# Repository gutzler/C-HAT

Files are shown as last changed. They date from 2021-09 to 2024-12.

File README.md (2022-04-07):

# C-HAT
Schematics and code for C-HAT loggers

Open-source, homebuilt dataloggers designed initially for work on lobsters.

C-HAT: Crustacean Heart and Activity Tracker

Arduino-based with substantial use of code snippets from Adafruit example libraries (among others).
Gutzler and Watson Highlight copy-1600

## Basic usage
Once the logger is built, set the clock with C-HAT_SetClock.ino, test the analog inputs with C-HAT_TestAnalogInputs.ino and the digital sensors with C-HAT_Accel_Mag_Test.ino, and check the SD card with the CardInfo example from the SD library. If all that works out, load the main code and go do some science!

### Important tips
- The heart sensor output is *NOT* the heart rate. It is raw readings from the analog-digital converter (ADC) on the board, so its values range from 0-1023 (10 bit logic). Plot these values out and use a peak finding algorithm to determine the rate of heartbeats. I use a (very expensive) program called LabChart, which is designed for physiological experiments; however, I've heard Python works well for that too, and R likely also has ways of doing it.
To go from ADC values to true voltage, divide the ADC output by the total number of possible values (1024), then multiply that value by the voltage of the board (3.3V). So, for ADC value of 500: (500/1024)x3.3V = 1.61V.
- The Real Time Clock chip is not smart enough to figure out Daylight Savings Time. Remember to reset it each time there's a time change!

### The Movement Index
To simplify analyses, I like to condense the triaxial acceleration values into a single number I refer to as the Movement Index. This is not done on the main board due to limited computing power, and I do it after the fact in other programs. The calculation is done by differentiating each axis of acceleration, squaring those values, combining them, and then taking the square root of the whole thing:

  https://latex.codecogs.com/svg.image?MI = \sqrt{(\textbf{differentiate}(accelX))^{2}+(\textbf{differentiate}(accelY))^{2}+(\textbf{differentiate}(accelZ))^{2}}

I use the Savitzy-Golay method and a three-sample window for the differentiation. At a 5 Hz sampling rate, this has the effect of magnifying short-term changes in acceleration (three samples is 0.6 seconds), more so than the longer windows typically used in the ODBA/VeDBA calculations often used in other accelerometer literature.

#### Implementing the MI in R:
```
library(prospectr)
...
#differentiate each axis using the Savitzky-Golay method
Xdiff <- savitzkyGolay(X=df1$accelX,m=1,p=1,w=3)
Ydiff <- savitzkyGolay(X=df1$accelY,m=1,p=1,w=3)
Zdiff <- savitzkyGolay(X=df1$accelZ,m=1,p=1,w=3)
#construct MI
NAobj <- as.vector("NA") #need this to build proper vectors
MI <- sqrt(Xdiff^2+Ydiff^2+Zdiff^2) #calculate MI
MI <- as.numeric(c(NAobj,MI,NAobj)) #the two added NA values are inserted because of the three sample window for differentiation
```

#### Implementing the MI in Python:
```
from numpy import square, sqrt
from scipy.signal import savgol_filter 
...
#differentiate each axis using the Savitzky-Golay method
df['dX'] = savgol_filter(df['accelX'],3,1,deriv=1)
df['dY'] = savgol_filter(df['accelY'],3,1,deriv=1)
df['dZ'] = savgol_filter(df['accelZ'],3,1,deriv=1)
#construct MI
df['MI'] = sqrt(square(df['dX'])+square(df['dY'])+square(df['dZ']))
```

### Helpful resources
The C-HAT code assumes a basic familiarity with Arduino boards, the Arduino language, and soldering together basic circuits. If you're just starting out, the [main Arduino website](https://www.arduino.cc/en/Guide) has many useful links and tips, including [examples that are excellent for practicing and learning](https://docs.arduino.cc/built-in-examples/), and their [language reference page](https://www.arduino.cc/reference/en/) is definitely worth bookmarking! Sparkfun has some [good beginner tutorials](https://learn.sparkfun.com/tutorials/what-is-an-arduino), including an [introduction to analog-digital converters](https://learn.sparkfun.com/tutorials/analog-to-digital-conversion) like those used for the heart sensor in the C-HAT.

Adafruit also has excellent tutorials and libraries for use of their boards.
The main "brains" of this setup is a pair of two Adafruit Feather boards, stacked using their short header pins. The main board is an [Adafruit 32u4 Featherlogger](https://learn.adafruit.com/adafruit-feather-32u4-adalogger) is Arduino-programmable and features the microSD card slot, while the [DS3231 Precision RTC Featherwing](https://learn.adafruit.com/adafruit-ds3231-precision-rtc-breakout/) stacks under the main board and requires no added wiring for its I2C communications (the header pins take care of that). The [LSM303AGR accelerometer](https://learn.adafruit.com/lsm303-accelerometer-slash-compass-breakout/downloads) also communicates over I2C - I like using Adafruit breakout boards because the Adafruit Sensor library package allows the output to be immediately displayed in standard units. Becoming familiar with using these boards is probably the best way to get ready to set up a C-HAT.

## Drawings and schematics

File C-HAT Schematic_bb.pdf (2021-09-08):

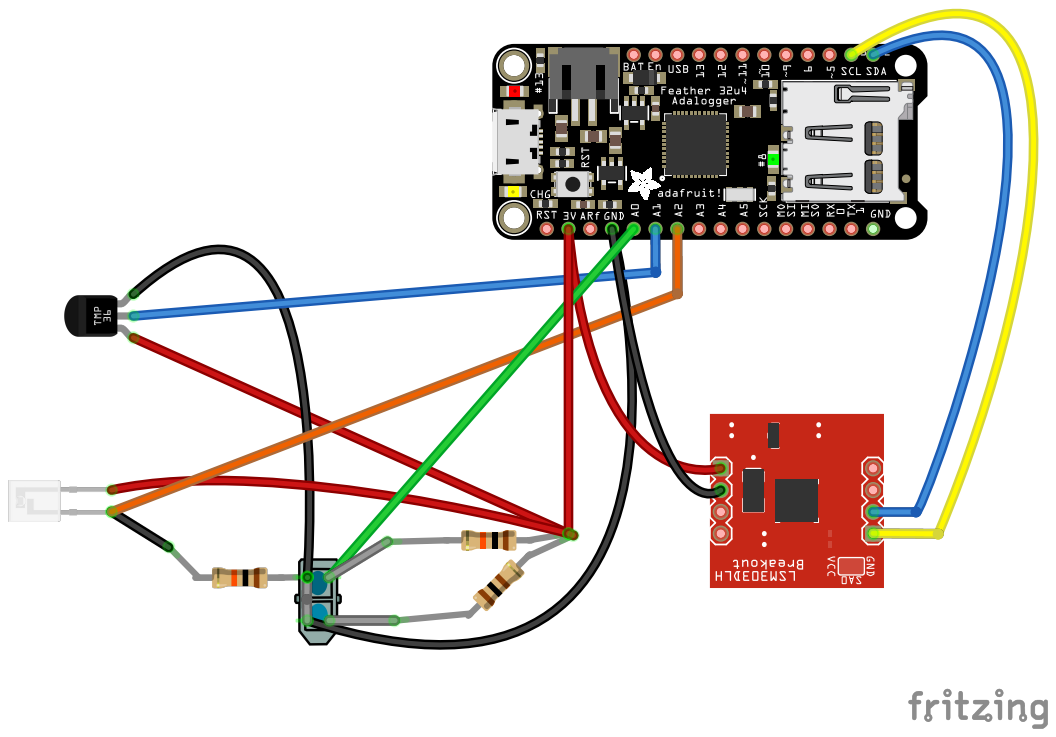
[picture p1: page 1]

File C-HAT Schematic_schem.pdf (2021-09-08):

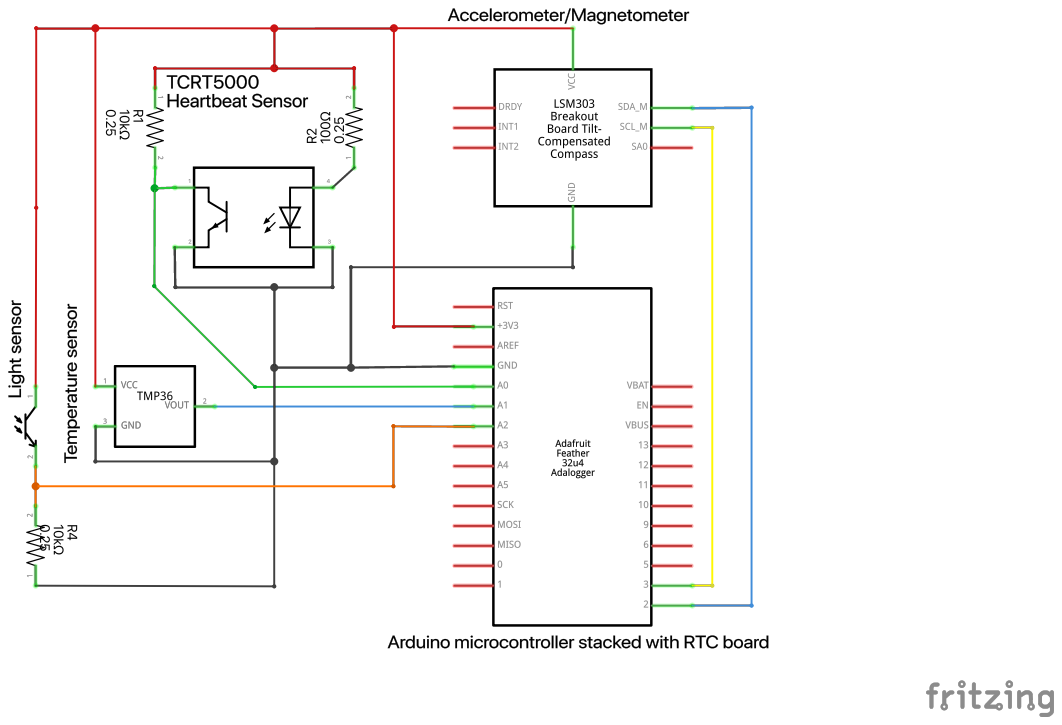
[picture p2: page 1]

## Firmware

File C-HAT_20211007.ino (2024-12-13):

/*Crustacean HAT Datalogger
 * (Heart and Activity Tracker)
 * v2.4 2021-10-7
 * Ben Gutzler bgutzler@gmail.com
 * Uses Adafruit Feather Adalogger, Adafruit DS3231 Precision RTC and LSM303 compass/accelerometer
 * along with TMP36 temp sensor, and HW5P phototransistor
 * Much code borrowed shamelessly from Adafruit examples
 * Tilt compensation now included on compass, based on Pololu and ST Microelectronics guides
 * Outputs a shedload of raw-ish data of pitch and roll to help decode heading later, maybe, if we ever figure out the tilt issues

*/

/*USAGE: connect power, then hit RESET button to ensure everything is starting at same time
 * If solid LED: something is not right
 * LED should flash every 4 seconds to indicate writing to SD card
 * Check this BEFORE starting trial!
 * Not a bad idea to check RTC is set either
 */
 
#include <Wire.h>
#include <SD.h>
#include <Adafruit_Sensor.h>
#include <Adafruit_LIS2MDL.h>
#include <Adafruit_LSM303_Accel.h>
#include "RTClib.h"


// LOGGING STUFF
// how many milliseconds between grabbing data and logging it. 1000 ms is once a second
  #define LOG_INTERVAL 200 // mills between entries (reduce to take more/faster data)

// how many milliseconds before writing the logged data permanently to disk
// set it to the LOG_INTERVAL to write each time (safest)
// set it to 10*LOG_INTERVAL to write all data every 10 datareads, you could lose up to 
// the last 10 reads if power is lost but it uses less power and is much faster!
  #define SYNC_INTERVAL 4000 // mills between calls to flush() - to write data to the card
  uint32_t syncTime = 0; // time of last sync()

#define ECHO_TO_SERIAL   1 // echo data to serial port

#define IRPin 0    //IR transceiver signal to A0
#define TempPin 1 // thermistor signal to A1
#define LightPin 2 // phototransistor signal to A2
#define statusPin 13 //D13 is red LED
#define errorPin 8 //D13 is green LED

RTC_DS3231 RTC;
  const int chipSelect = 4; //SS pin on Featherlogger
  File logfile; // the logging file

 //defining how to read the uncalibrated data
  int IRReading;
  int TempReading;
  int LightReading;
  float accelX = 0.00;
  float accelY = 0.00;
  float accelZ = 0.00;
  float TempV;
  float TempC;

  // this should let me take more than one measurement per second and keep them straight
  unsigned long millis_now;
  unsigned long millis_prev = 0;
  int millis_diff;
  uint16_t seconds_now;
  uint16_t seconds_prev = 0;

/* Assign a unique ID to this sensor at the same time */
Adafruit_LIS2MDL mag = Adafruit_LIS2MDL(12345);
Adafruit_LSM303_Accel_Unified accel = Adafruit_LSM303_Accel_Unified(54321);

  sensors_event_t a, m;

void error(char const *str)
{
  Serial.print("error: ");
  Serial.println(str);
  digitalWrite(errorPin, HIGH);
  digitalWrite(statusPin, HIGH);
   while (1){ //This loops to make the lights blink on and off to make it clear there's an issue
    delay(200);
    digitalWrite(errorPin, LOW);
    digitalWrite(statusPin, LOW);
    delay(200);
    digitalWrite(errorPin, HIGH);
    digitalWrite(statusPin, HIGH);
   }
}


void setup(void) 
{
  Serial.begin(9600);
 Serial.println();

  pinMode(IRPin, INPUT);
  pinMode(TempPin, INPUT);
  pinMode(LightPin, INPUT);

  // initialize the SD card
  pinMode(10, OUTPUT);

  // let it know the light pins are output only
  pinMode(8, OUTPUT);
  //pinMode(13, OUTPUT);
  /*pin 13 blinks most often, and setting to OUTPUT allows it to
   * dump a lot more current into lighting up the LED - it's fine without
   * and saves us some power!
   */
  
  // see if the card is present and can be initialized:
  if (!SD.begin(chipSelect)) {
    error("Card failed, or not present");
  }
  Serial.println("card initialized.");
  
  // create a new file
  char filename[] = "HATLOG00.CSV";
  for (uint8_t i = 0; i < 100; i++) {
    filename[6] = i/10 + '0';
    filename[7] = i%10 + '0';
    if (! SD.exists(filename)) {
      // only open a new file if it doesn't exist
      logfile = SD.open(filename, FILE_WRITE); 
      break;  // leave the loop!
    }
  }
  
  if (! logfile) {
    error("couldn't create file");
    digitalWrite(errorPin, HIGH);
  }

  // connect to RTC
  Wire.begin();  
  if (!RTC.begin()) {
    error("RTC failed");
    digitalWrite(errorPin, HIGH);
  }
 
  if(!mag.begin())
  {
    /* There was a problem detecting the LIS2MDL ... check your connections */
    error("Ooops, no LIS2MDL detected ... Check your wiring!");
    while(1);
  }
  if (!accel.begin()) {
    /* There was a problem detecting the LSM303 ... check your connections */
    error("Ooops, no LSM303 Accelerometer detected ... Check your wiring!");
    while (1)
      ;
  }
 
  //THIS IS WHAT GETS LOGGED
  logfile.println("datetime,heartIR,accelX,accelY,accelZ,hdg_uncomp,hdgcompensated,temp,light,roll,pitch,magX,magY,magZ");    
#if ECHO_TO_SERIAL
  Serial.println("datetime,heartIR,accelX,accelY,accelZ,hdg_uncomp,hdgcompensated,temp,light,roll,pitch,magX,magY,magZ");
#endif //ECHO_TO_SERIAL

}

// ACTUALLY RUNNING THIS
void loop(void) 
{ 
  DateTime now;

  // delay for the amount of time we want between readings
  delay((LOG_INTERVAL -1) - (millis() % LOG_INTERVAL));

  digitalWrite(statusPin, LOW); //making LED blink when writing to SD
    //easier to see if it's still running or the battery is dead
  
  // fetch the time
  now = RTC.now();

  seconds_now = now.second();
  millis_now = millis();
  millis_diff = millis_now - millis_prev;
  if (millis_diff > 900) {
    millis_diff = 0;
  }
  if (seconds_prev != seconds_now) {
    seconds_prev = seconds_now;
    millis_prev = millis_now;
   }

  //Get analog sensor readings
  IRReading = analogRead(IRPin);
  TempReading = analogRead(TempPin);
  LightReading = analogRead(LightPin);

  //Convert analog temp input to degrees C
  //The next block of code is an expansion of this: TempC = ((TempReading*3.3)*100)-50;
    TempV = TempReading*3.3;
    TempC=TempV/1024; //equivalent to saying "TempC = previous value of TempC * 100"
    TempC-=.5; 
    TempC*=100;
  
  /* Get new sensor events */ 
 // sensors_event_t a, m;
  accel.getEvent(&a);
  mag.getEvent(&m);

   accelX = a.acceleration.x;
   accelY = a.acceleration.y;
   accelZ = a.acceleration.z;

/*
 * This big chunk of code does the tilt compensation.
 * It works together with a couple functions at the bottom to calculate pitch and roll.
 * I got the math from a post on the Pololu forums: https://forum.pololu.com/t/lsm303d-tilt-compensation-problem/11611
 * Kevin at Pololu wrote Heading2.ino which formed the base of the math.
 * I adapted some of the pitch and roll equations from ST Microelectronics app note DT0058 "Computing tilt measurement and tilt-compensated e-compass"
 * https://www.st.com/content/ccc/resource/technical/document/design_tip/group0/56/9a/e4/04/4b/6c/44/ef/DM00269987/files/DM00269987.pdf/jcr:content/translations/en.DM00269987.pdf
 * I could've used an existing Pololu library with the LSM303DLHC, but I'm trying to futureproof.
 */

  int32_t temp_mx = mag.raw.x;
  int32_t temp_my = mag.raw.y;
  int32_t temp_mz = mag.raw.z;  

 //Uncomment this next section if you want to calibrate each LSM303 chip - leaving it commented sticks with factory calibration
  // doing math for offsets from empirical calibration values - these values are from the testbed version at Wells 2020/2/6
     /*    min   max   avg
      * x  -407  177   -115
      * y  -405  271   -67
      * z  -540  134   -203
     */

  /* 
  int32_t temp_mx -= (-115);
  int32_t temp_my -=  (-67);
  int32_t temp_mz -= (-203);
 */
 
/*Heading calculations*/
//h1 = uncompensated Adafruit code
float h1 = (atan2(mag.raw.y,mag.raw.x) * 180) / PI;
 if (h1 < 0) h1 += 360;

//hcomp = from https://www.instructables.com/id/Tilt-Compensated-Compass/
float Mag_roll = (atan2(a.acceleration.y, a.acceleration.z)*(180/PI));
float Mag_pitch = (atan(-a.acceleration.x/((a.acceleration.y * sin(atan2(a.acceleration.y, a.acceleration.z)) + a.acceleration.z * cos(atan2(a.acceleration.y, a.acceleration.z))))))*(180/PI);
float Xhorizontal = accelX*cos(Mag_pitch) + accelY*sin(Mag_roll)*sin(Mag_pitch) - accelZ*cos(Mag_roll)*sin(Mag_pitch);
float Yhorizontal = accelY*cos(Mag_roll) + accelZ*sin(Mag_roll);
float hcomp = atan2(Yhorizontal,Xhorizontal) * 180 / PI;
  if (hcomp < 0) hcomp += 360;

//end of the tilt compensation and heading calculation bit

  
// log time and data
  logfile.print('"');
  logfile.print(now.year(), DEC);
  logfile.print("/");
  logfile.print(now.month(), DEC);
  logfile.print("/");
  logfile.print(now.day(), DEC);
  logfile.print(" ");
  logfile.print(now.hour(), DEC);
  logfile.print(":");
  logfile.print(now.minute(), DEC);
  logfile.print(":");
  logfile.print(now.second(), DEC);
  logfile.print(".");
  logfile.print(millis_diff);
  logfile.print('"');
  logfile.print(", ");    
  logfile.print(IRReading); //to get from IR reading to voltage: IRreading*3.3/1024
  logfile.print(", ");    
  logfile.print(accelX);
  logfile.print(", ");
  logfile.print(accelY);
  logfile.print(", ");
  logfile.print(accelZ);
  logfile.print(", ");    
  logfile.print(h1);
  logfile.print(", "); 
  logfile.print(hcomp); //this is VERY noisy - will want to smooth afterwards
  logfile.print(", ");
  logfile.print(TempC); //TMP36 outputs straight to ºC
  logfile.print(", ");    
  logfile.print(LightReading); //to get from reading to voltage: reading*3.3/1024
  logfile.print(", ");    
  logfile.print(Mag_roll);
  logfile.print(", ");
  logfile.print(Mag_pitch);
  logfile.print(", ");
  logfile.print(temp_mx);
  logfile.print(", ");
  logfile.print(temp_my);
  logfile.print(", ");
  logfile.print(temp_mz);
  logfile.println();
#if ECHO_TO_SERIAL
  Serial.print('"');
  Serial.print(now.year(), DEC);
  Serial.print("/");
  Serial.print(now.month(), DEC);
  Serial.print("/");
  Serial.print(now.day(), DEC);
  Serial.print(" ");
  Serial.print(now.hour(), DEC);
  Serial.print(":");
  Serial.print(now.minute(), DEC);
  Serial.print(":");
  Serial.print(now.second(), DEC);
  Serial.print(".");
  Serial.print(millis_diff);
  Serial.print('"');
  Serial.print(", ");   
  Serial.print(IRReading);
  Serial.print(", ");
  Serial.print(accelX,4);
  Serial.print(", ");
  Serial.print(accelY,4);
  Serial.print(", "); 
  Serial.print(accelZ,4);
  Serial.print(", ");
  Serial.print(h1);
  Serial.print(", "); 
  Serial.print(hcomp);
  Serial.print(", ");    
  Serial.print(TempC);
  Serial.print(", ");
  Serial.print(LightReading);
  Serial.print(", "); 
  Serial.print(Mag_roll);
  Serial.print(", "); 
  Serial.print(Mag_pitch);
  Serial.print(", ");
  Serial.print(temp_mx);
  Serial.print(", ");
  Serial.print(temp_my);
  Serial.print(", ");
  Serial.print(temp_mz);
 Serial.println();
#endif //ECHO_TO_SERIAL

 
// Now we write data to disk! Don't sync too often - requires 2048 bytes of I/O to SD card
  // which uses a bunch of power and takes time
  if ((millis() - syncTime) < SYNC_INTERVAL) return;
  syncTime = millis();
  logfile.flush();
  digitalWrite(statusPin, HIGH);
}

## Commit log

2021-09-08 Fritzing files
    [C-HAT Schematic.fzz]
2021-10-07 Arduino code
    Basic code for logger - not including calibration files or examples
2021-10-29 Adding test/troubleshoot Arduino code
    Arduino sketches for setup and troubleshooting of C-HAT loggers
2023-07-28 Update Parts List
    Added runtime/power consumption line
2024-12-23 Delete C-HAT_20211007.ino
    This is the old C-HAT without the mandible sensor
